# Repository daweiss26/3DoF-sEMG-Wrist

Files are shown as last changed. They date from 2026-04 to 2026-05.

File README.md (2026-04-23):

# Orbita3D Setup Instructions

---

## Prerequisites

You need the following installed on your system:

* **Rust:** Used for compiling the kinematics SDK
* **Python (v3.12 Preferred):** Runs the controller

*Note: These instructions use python and pip commands. You may need to use python3 or pip3 depending on your setup.*

---

## Virtual Environment

It is recommended to create a virtual environment to store compiled packages

*Note: If using PowerShell, you may need to run ```
Set-ExecutionPolicy -ExecutionPolicy RemoteSigned -Scope Process``` first if activation is disabled.*

Create virtual environment (.venv recommended: Other environment names may require file changes such as run_camera_demo.bat)
```
python -m venv .venv
```

Activate virtual environment
```
.venv\Scripts\activate // Windows
source .venv/bin/activate // Mac/Linux
```

---

## Installation

Install the dependencies in the requirements.txt file:
```
pip install -r requirements.txt
```

Then install the Orbita3D package. Inside ```orbita3d_control/orbita3d_c_api```, run:
```
pip install -e .
```

---

## Firmware

Upload the Orbitarduinamixel project to your Generic STM32G4 Series device. Custom-installed libraries should be included in the project.

You may need to add the following .json file for additional boards in the Board Manager:
```
https://github.com/stm32duino/BoardManagerFiles/raw/main/package_stmicroelectronics_index.json
```

The libraries installed:
* **[Simple FOC](https://docs.simplefoc.com/):** by Simplefoc
* **[SimpleFOCDrivers](https://docs.simplefoc.com/):** by Simplefoc
* **[Dynamixel2Arduino](https://github.com/ROBOTIS-GIT/dynamixel2arduino):** by ROBOTIS
* **[Bolder Flight Systems BMI088](https://github.com/bolderflight/bmi088-arduino):** by Brian Taylor

---

## Use

*If using VSCode (recommended), ensure the project contains a ```.vscode``` file with:*
```
{
    "python-envs.defaultEnvManager": "ms-python.python:venv",
    "python.terminal.useEnvFile": true
}
```
Or, in your terminal, ```".:./src:./src/controller:./src/util"``` to your PYTHONPATH environment variable, such as with ```export PYTHONPATH=".:./src:./src/controller:./src/util:$PYTHONPATH"``` for Mac/Linux. For Windows, ```run_camera_demo.bat``` should take care of this.

If using Windows: running ```run_camera_demo.bat``` should work. *Note: You may need to change the specific virtual environment listed in the .bat file if you are using something different from .venv*

If using Mac/Linux: simply run a demo script from the project root directory such as ```python src/orbita_abh_camera.py```

*Note: If using a demo script, you will need to change the Ability Hand serial port in ```src/orbita_abh_camera.py``` and the Orbita3D serial port in ```config/default.yaml``` based upon your device setup. You will likely also need to alter the camera index in ```src/orbita_abh_camera.py``` depending on your setup.*

* **orbita_abh_camera.py:** Uses camera landmarks
* **orbita_emg.py:** Uses muscular signal and a residual TCN model
* **orbita_emg_krr.py:** Uses muscular signal and a kernel ridge regression model
* **task:** Contains landmarker tasks
* **config:** Contains .yaml files for Orbita3D setup. *Contains the serial port to use, which is determined by your specific device.*
* **orbita3d_control:** Contains kinematics for Orbita3D control.
* **firmware:** Contains Arduino code for Orbita3D
* **src/controller:** Contains controller classes for Orbita3D and Ability Hand
* **src/data_collection:** Contains tools for determining electromechanical delay and collecting data
* **src/train:** Contains tools for training muscular signal decoders using collected data
* **src/util:** Contains utilities such as the pose landmarker and coordinate transformer classes

---

## Sources

* **[Orbita3D](https://github.com/pollen-robotics/Orbita_3d_R1):** Original actuator design
* **[Orbita3D Control](https://github.com/pollen-robotics/orbita3d_control):** Generates the kinematics SDK
* **[Rustypot](https://github.com/pollen-robotics/rustypot):** Used to configure servos
* **[Ability Hand API](https://github.com/psyonicinc/ability-hand-api):** Reference on controlling PSYONIC Ability Hand

---

## Docker

You can also run the camera demo through Docker instead of creating a local Python environment if you are using Linux or an OS where Docker is not run on a virtual machine. The Docker image installs the Python dependencies from `requirements.txt`, builds and installs the local `orbita3d_control/orbita3d_c_api` package, and starts `src/orbita_abh_camera.py`.

### Build the image

From the project root, run:
```
docker build --platform linux/amd64 -t orbita-camera-demo .
```

### Run the container

The script needs access to your camera and, if you are controlling hardware, your serial devices. It also opens an OpenCV display window, so on Linux you will typically need to share your X11 socket. A common Linux example is:

```
docker run --platform linux/amd64 --rm -it \
  --device /dev/video0:/dev/video0 \
  --device /dev/ttyUSB0:/dev/ttyUSB0 \
  -e DISPLAY=$DISPLAY \
  -v /tmp/.X11-unix:/tmp/.X11-unix \
  orbita-camera-demo \
  --camera_index 0 \
  --hand_port /dev/ttyUSB0 \
  --orbita_config ./config/default.yaml
```

### Notes

* Update `config/default.yaml` so its `serial_port` matches the Orbita device inside the container, such as `/dev/ttyUSB1` or `/dev/serial/by-id/...`.
* The Ability Hand port is now configurable through `--hand_port`, which is helpful because Linux device names differ from macOS names such as `/dev/cu.usbserial-*`.
* If you only want to test the vision pipeline without connected hardware, you can add `--disable_wrist --disable_hand`.
* If your camera is exposed under a different device path or index, adjust `--device` and `--camera_index` accordingly.
* On macOS or Windows, Docker Desktop does not pass host cameras and serial devices into Linux containers as directly as native Linux does. For full hardware access, running the container on a Linux host is the simplest path.

### Pass different script arguments

Anything placed after the image name is forwarded to `src/orbita_abh_camera.py`. For example:

```
docker run --rm -it \
  --device /dev/video0:/dev/video0 \
  -e DISPLAY=$DISPLAY \
  -v /tmp/.X11-unix:/tmp/.X11-unix \
  orbita-camera-demo \
  --disable_wrist --disable_hand --camera_index 0 --use_elbow
```

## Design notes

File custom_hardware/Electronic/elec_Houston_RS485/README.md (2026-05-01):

# Houston Electronic Board

Houston board is basically a STM32G4 microcontroller that focuses on driving 3 BLDC motors. It gets 3 Hall effects or encoders on motors and absolute positions behind reduction through SPI encoders.

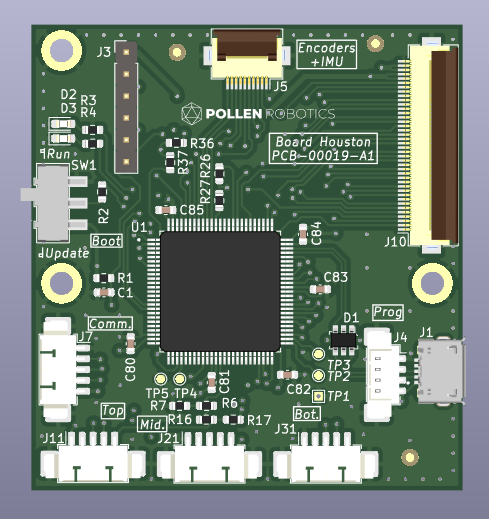
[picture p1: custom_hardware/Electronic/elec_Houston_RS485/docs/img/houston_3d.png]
houston board 3d image


## Basically
 - 50 x 54 mm
 - Powered in 3V3 through the large flat flexible connector J10
 - 5V should also be provided since it supplies encoders J11/21/31
 - Designed with KiCAD 6.0

## ST configuration

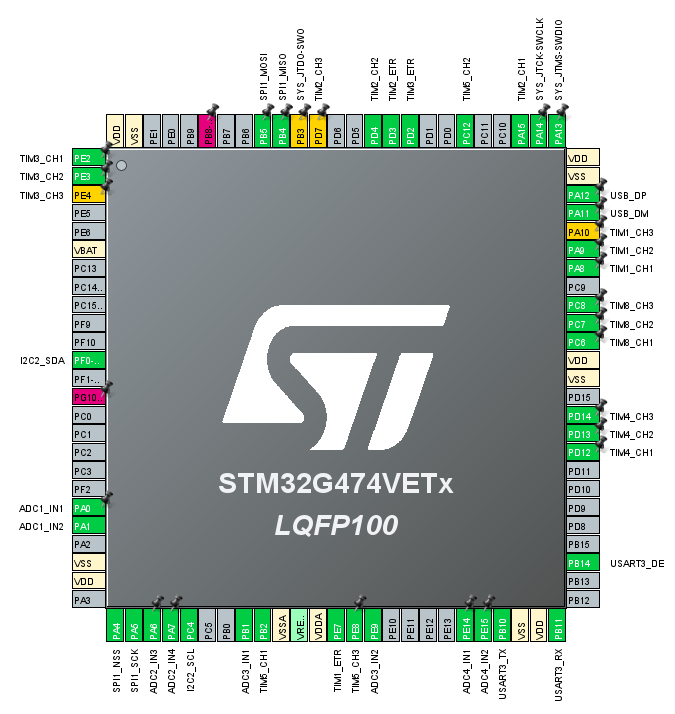
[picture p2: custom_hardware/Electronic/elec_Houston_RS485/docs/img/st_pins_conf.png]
houston board 3d image


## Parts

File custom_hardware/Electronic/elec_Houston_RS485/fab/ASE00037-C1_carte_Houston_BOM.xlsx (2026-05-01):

ASE00037 | C1 | Houston | 2023-04-14
Ref. | Value | Description | Qtty | Man. | Man. Ref.
C1, C80, C81, C82, C83, C84, C85 | 100n 6V3 | Capa 0603 | 7 | TDK | CGA3E2X7R1H104K080AA
D1 | USBLC6-2SC6 | ESD Protection | 1 | STMicro | USBLC6-2SC6
D2 | Green | Green LED 0603 | 1 | Wurth | 150060VS75000
D3 | Red | Red LED 0603 | 1 | Wurth | 150060RS75000
H5 | PCB00019 | PCB | 1
J1 | 10118194-0001LF | USB Prog Connector | 1 | Amphenol FCI | 10118194-0001LF
J2 | Pico3 | Comm. Connector | 1 | Molex | 53261-0371
J3 | DNP - SIL6 | SWDebug Connector | 1 | Harwin | M20-9990646
J4 | Pico4 | Fake USB Connector | 1 | Molex | 53398-0471
J5 | FFC 0,5 mm 10w | Encoders/IMU Connector | 1 | Hirose | FH12-10S-0.5SH(55)
J11, J21, J31 | Pico5 | Comm. Connector | 3 | Molex | 53261-0571
J10 | FFC 0,5 mm 40w | Microcontroller Connector | 1 | Hirose | FH12-40S-0.5SH(55)
R1 | 100k | Res. 0603 | 1 | Yageo | RC0603FR-07100KL
R2 | 10k | Res. 0603 | 1 | Yageo | RC0603FR-0710KL
R3, R4 | 470R | Res. 0603 | 2 | Yageo | RC0603FR-07470RL
R6 | DNP-4k7 | Res. 0603 | 1
R7 | DNP-9k1 | Res. 0603 | 1
R17, R27, R38, R39 | 0R | Res. 0603 | 4 | Yageo | RC0603FR-070RL
R26, R36, R37, R40 | DNP-0R | Res. 0603 | 4
SW1 | SW_SPDT | Boot switch | 1 | C&K Switches | JS102011SAQN
U1 | STM32G474 | Microcontroller | 1 | STMicro | STM32G474VET6

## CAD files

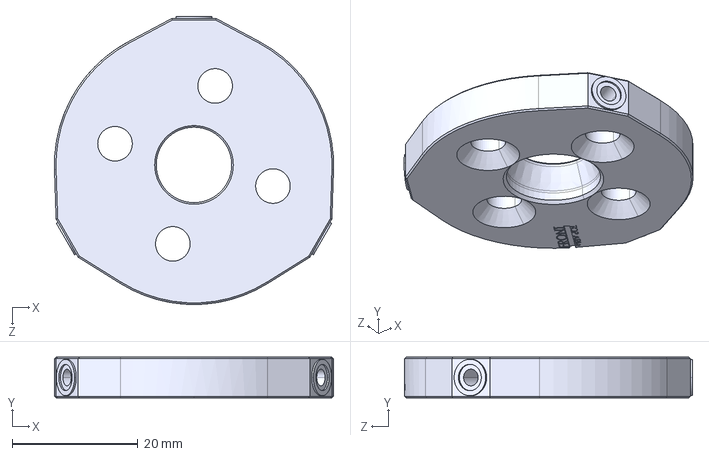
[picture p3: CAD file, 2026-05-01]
custom_hardware/Mechanical/Adapter/ResearchWristAdapter.STEP
44.4 x 6.50 x 45.8 mm

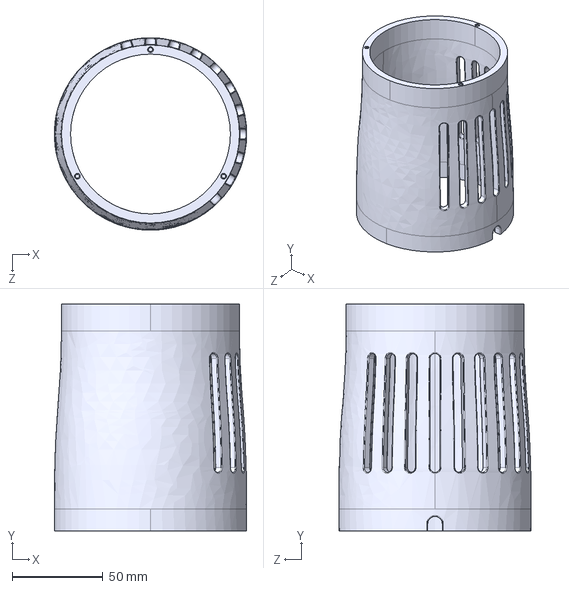
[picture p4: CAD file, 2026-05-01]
custom_hardware/Mechanical/Enclosure/EnclosureBody.STEP
106.0 x 125.0 x 106.0 mm

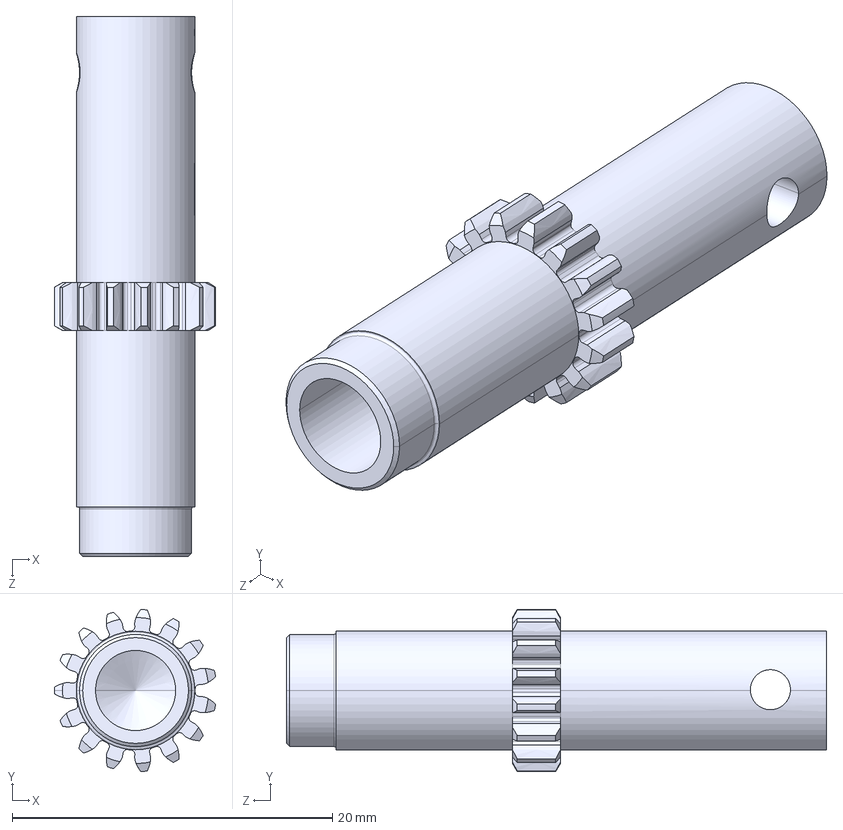
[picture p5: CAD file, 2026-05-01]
custom_hardware/Mechanical/Gears/MiddlePinion.STEP
10.1 x 10.1 x 33.7 mm

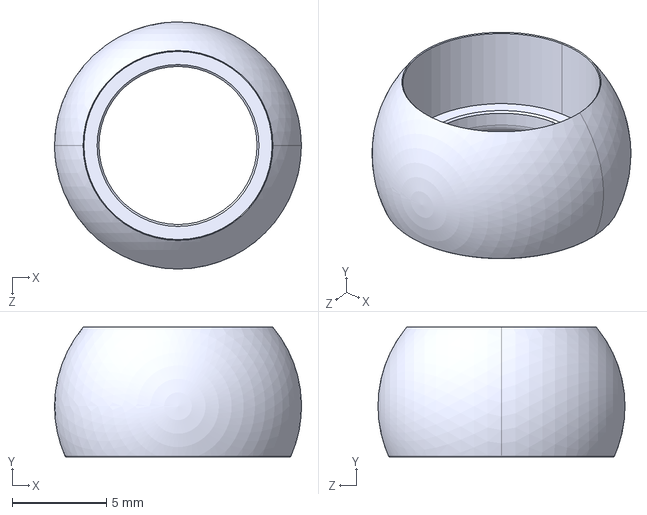
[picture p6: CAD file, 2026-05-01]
custom_hardware/Mechanical/Adapter/ResearchBall.STEP
13.1 x 6.89 x 13.1 mm

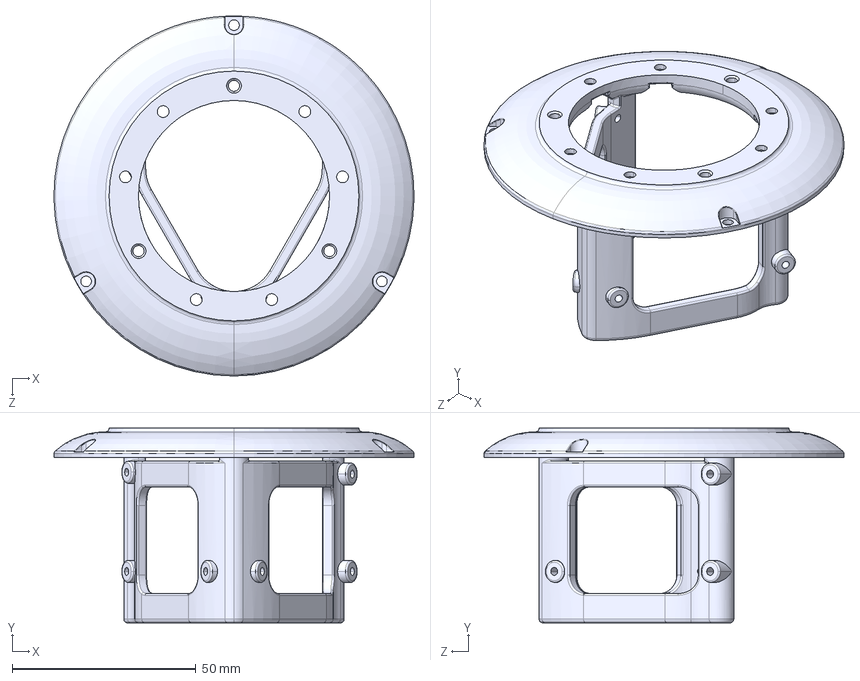
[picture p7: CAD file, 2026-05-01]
custom_hardware/Mechanical/Enclosure/EnclosureTopWithPCBHolder.STEP
98.0 x 53.0 x 98.0 mm

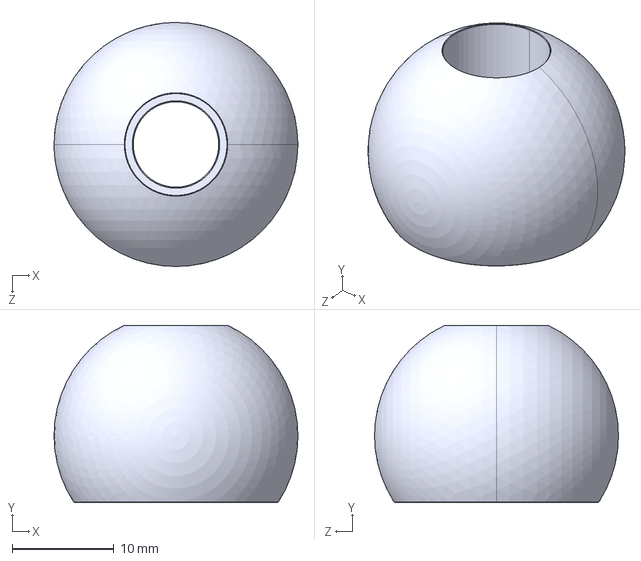
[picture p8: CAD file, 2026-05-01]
custom_hardware/Mechanical/Adapter/LaminationBall.STEP
24.0 x 17.5 x 24.0 mm

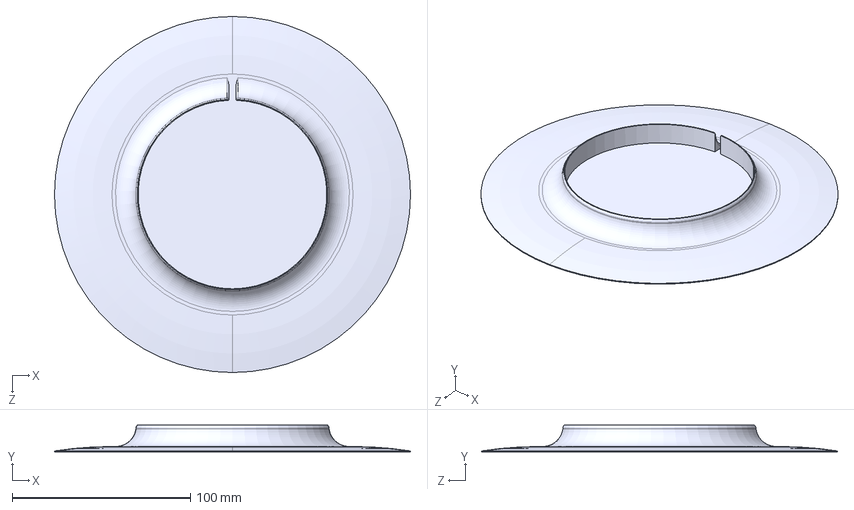
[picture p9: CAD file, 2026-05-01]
custom_hardware/Mechanical/Enclosure/EnclosureBottom.STEP
200.0 x 15.0 x 200.0 mm

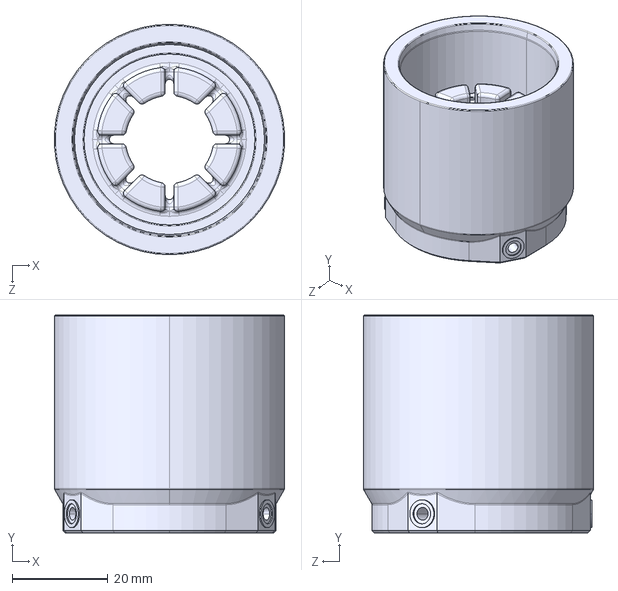
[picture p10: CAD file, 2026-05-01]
custom_hardware/Mechanical/Adapter/LaminationWristAdapter.STEP
47.9 x 45.4 x 48.0 mm

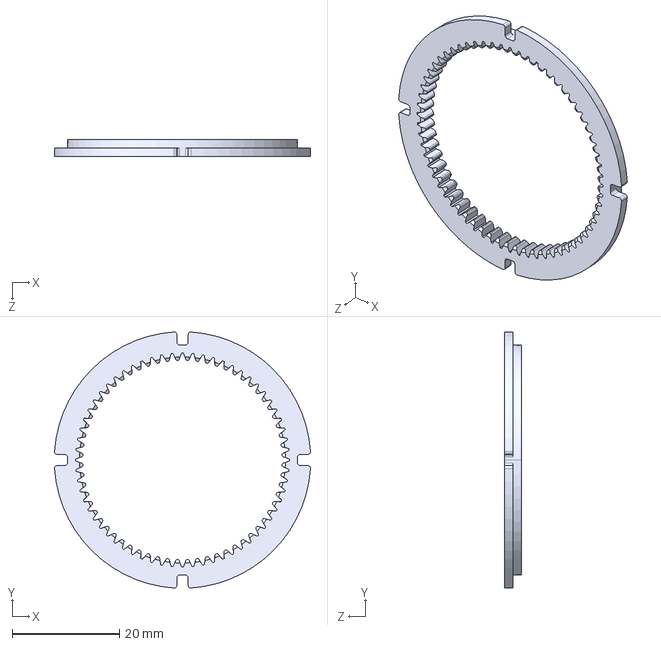
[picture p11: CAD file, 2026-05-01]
custom_hardware/Mechanical/Gears/InternalGear.STEP
47.8 x 47.8 x 3.20 mm

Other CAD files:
custom_hardware/Mechanical/Gears/TopPinion.STEP
custom_hardware/Mechanical/Gears/BottomPinion_Dslot.STEP
custom_hardware/Mechanical/Gears/MiddlePinion_Dslot.STEP
custom_hardware/Mechanical/Gears/TopPinion_Dslot.STEP
custom_hardware/Mechanical/Gears/BottomPinion.STEP

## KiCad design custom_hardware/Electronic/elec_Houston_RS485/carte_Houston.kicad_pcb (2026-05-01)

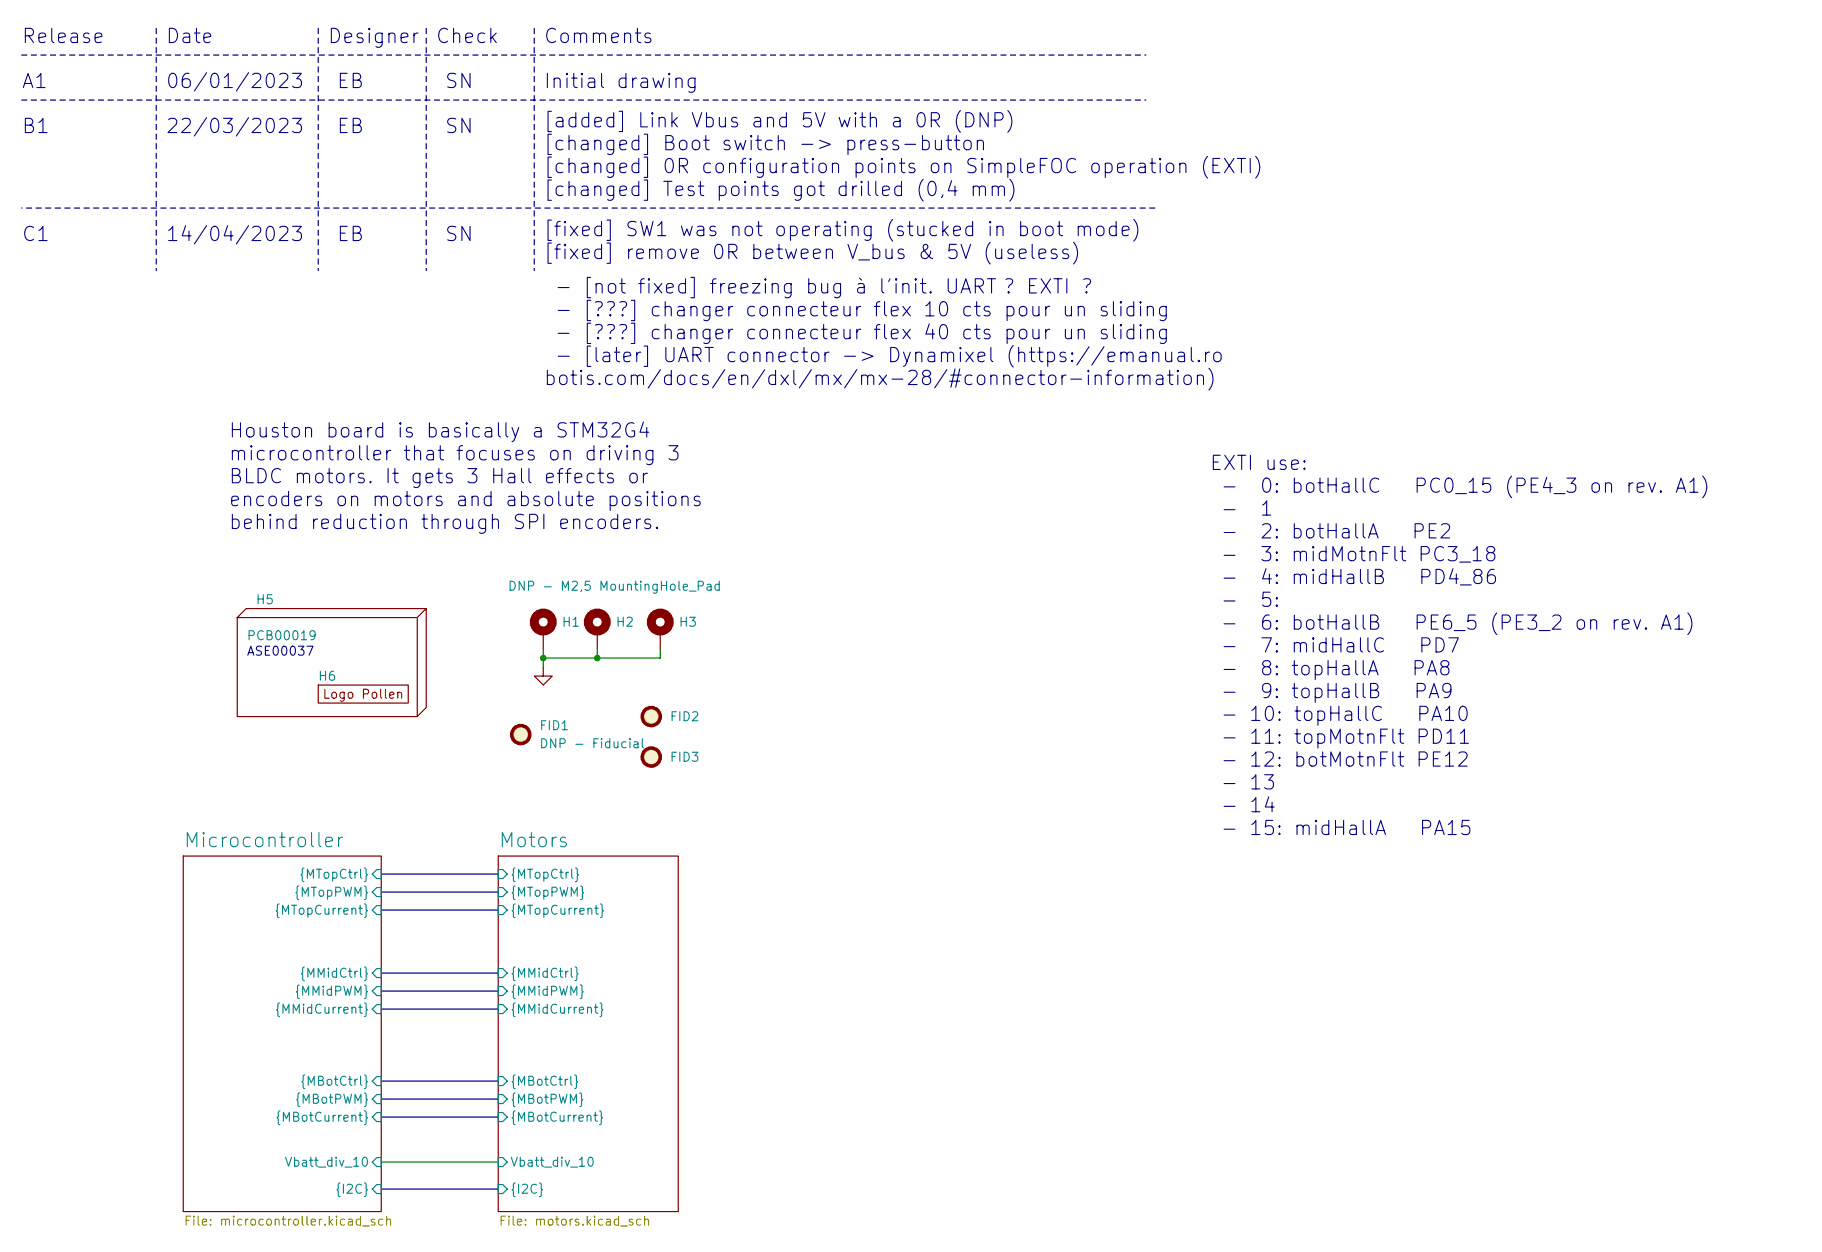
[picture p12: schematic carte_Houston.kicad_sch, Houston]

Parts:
FID1, FID2, FID3: DNP - Fiducial; Fiducial_1mm_Mask2mm
H1, H2, H3: DNP - M2,5 MountingHole_Pad; MountingHole_2.7mm_M2.5_DIN965_Pad_TopOnly
H5: PCB00019
H6: DNP - Logo Pollen 2021; Logo_Pollen_2021

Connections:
GND: H1.1, H2.1, H3.1; also elsewhere on the board

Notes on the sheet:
Date
Check
Release
[added] Link Vbus and 5V with a 0R (DNP) [changed] Boot switch -> press-button [changed] 0R configuration points on SimpleFOC operation (EXTI) [changed] Test points got drilled (0,4 mm)
ASE00037
22/03/2023
- [not fixed] freezing bug à l'init. UART ? EXTI ? - [???] changer connecteur flex 10 cts pour un sliding - [???] changer connecteur flex 40 cts pour un sliding - [later] UART connector -> Dynamixel (https://emanual.ro botis.com/docs/en/dxl/mx/mx-28/#connector-information)
Initial drawing
[fixed] SW1 was not operating (stucked in boot mode) [fixed] remove 0R between V_bus & 5V (useless)
EXTI use: - 0: botHallC PC0_15 (PE4_3 on rev. A1) - 1 - 2: botHallA PE2 - 3: midMotnFlt PC3_18 - 4: midHallB PD4_86 - 5: - 6: botHallB PE6_5 (PE3_2 on rev. A1) - 7: midHallC PD7 - 8: topHallA PA8 - 9: topHallB PA9 - 10: topHallC PA10 - 11: topMotnFlt PD11 - 12: botMotnFlt PE12 - 13 - 14 - 15: midHa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
Designer
14/04/2023
Houston board is basically a STM32G4 microcontroller that focuses on driving 3 BLDC motors. It gets 3 Hall effects or encoders on motors and absolute positions behind reduction through SPI encoders.
Comments
06/01/2023

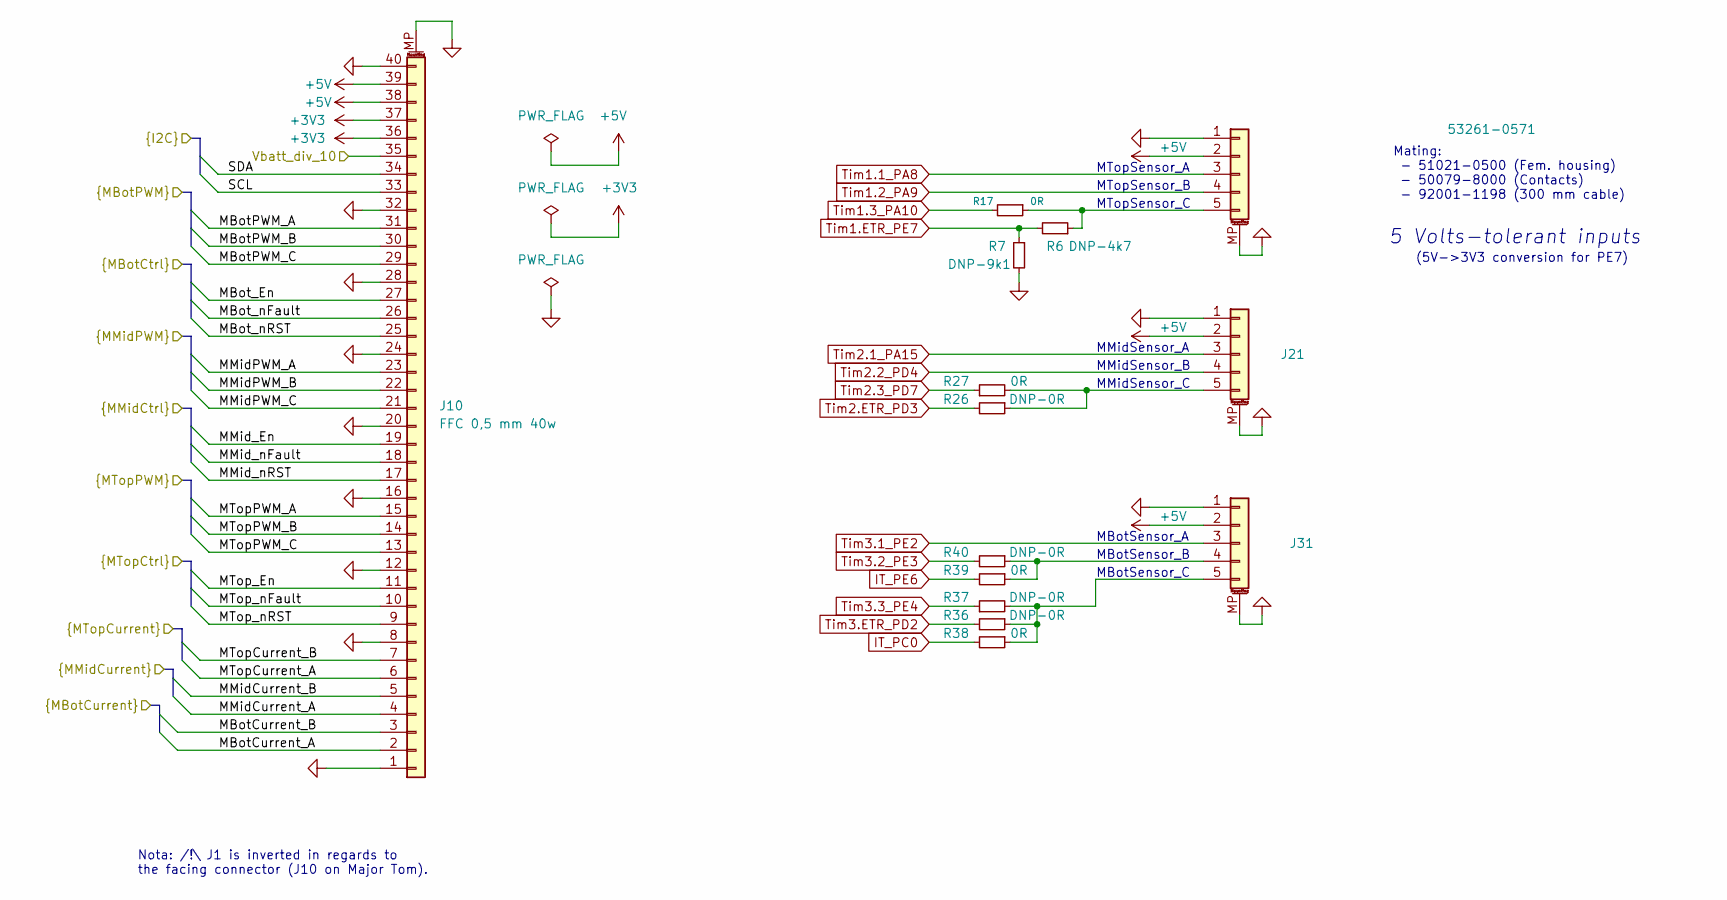
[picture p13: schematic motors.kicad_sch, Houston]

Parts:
J10: FFC 0,5 mm 40w; Hirose_FH12-40S-0.5SH_1x40-1MP_P0.50mm_Horizontal
J11: PicoBlade5; Molex_PicoBlade_53261-0571_1x05-1MP_P1.25mm_Horizontal
J21, J31: Pico5; Molex_PicoBlade_53261-0571_1x05-1MP_P1.25mm_Horizontal
R6: DNP-4k7; R_0603_1608Metric
R7: DNP-9k1; R_0603_1608Metric
R17, R27, R38, R39: 0R; R_0603_1608Metric
R26, R36, R37, R40: DNP-0R; R_0603_1608Metric

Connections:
+3V3: J10.36, J10.37; also elsewhere on the board
+5V: J10.38, J10.39, J11.2, J21.2, J31.2; also elsewhere on the board
/Microcontroller/MBotCurrent_A: J10.2; also elsewhere on the board
/Microcontroller/MBotCurrent_B: J10.3; also elsewhere on the board
/Microcontroller/MBotPWM_A: J10.31; also elsewhere on the board
/Microcontroller/MBotPWM_B: J10.30; also elsewhere on the board
/Microcontroller/MBotPWM_C: J10.29; also elsewhere on the board
/Microcontroller/MBot_En: J10.27; also elsewhere on the board
/Microcontroller/MBot_nFault: J10.26; also elsewhere on the board
/Microcontroller/MBot_nRST: J10.25; also elsewhere on the board
/Microcontroller/MMidCurrent_A: J10.4; also elsewhere on the board
/Microcontroller/MMidCurrent_B: J10.5; also elsewhere on the board
/Microcontroller/MMidPWM_A: J10.23; also elsewhere on the board
/Microcontroller/MMidPWM_B: J10.22; also elsewhere on the board
/Microcontroller/MMidPWM_C: J10.21; also elsewhere on the board
/Microcontroller/MMid_En: J10.19; also elsewhere on the board
/Microcontroller/MMid_nFault: J10.18; also elsewhere on the board
/Microcontroller/MMid_nRST: J10.17; also elsewhere on the board
/Microcontroller/MTopCurrent_A: J10.6; also elsewhere on the board
/Microcontroller/MTopCurrent_B: J10.7; also elsewhere on the board
/Microcontroller/MTopPWM_A: J10.15; also elsewhere on the board
/Microcontroller/MTopPWM_B: J10.14; also elsewhere on the board
/Microcontroller/MTopPWM_C: J10.13; also elsewhere on the board
/Microcontroller/MTop_En: J10.11; also elsewhere on the board
/Microcontroller/MTop_nFault: J10.10; also elsewhere on the board
/Microcontroller/MTop_nRST: J10.9; also elsewhere on the board
/Microcontroller/SCL: J10.33; also elsewhere on the board
/Microcontroller/SDA: J10.34; also elsewhere on the board
/Microcontroller/Vbatt_div_10: J10.35; also elsewhere on the board
GND: J10.1, J10.8, J10.12, J10.16, J10.20, J10.24, J10.28, J10.32, J10.40, J10.MP (MountPin), J11.1, J11.MP (MountPin), J21.1, J21.MP (MountPin), J31.1, J31.MP (MountPin), R7.2; also elsewhere on the board
IT_PC0: R38.2; also elsewhere on the board
IT_PE6: R39.2; also elsewhere on the board
unnamed: J11.5, R6.1, R17.1
unnamed: J21.5, R26.1, R27.2
unnamed: J31.4, R39.1, R40.1
unnamed: J31.5, R36.1, R37.2, R38.1
Tim1.1_PA8: J11.3; also elsewhere on the board
Tim1.2_PA9: J11.4; also elsewhere on the board
Tim1.3_PA10: R17.2; also elsewhere on the board
Tim1.ETR_PE7: R6.2, R7.1; also elsewhere on the board
Tim2.1_PA15: J21.3; also elsewhere on the board
Tim2.2_PD4: J21.4; also elsewhere on the board
Tim2.3_PD7: R27.1; also elsewhere on the board
Tim2.ETR_PD3: R26.2; also elsewhere on the board
Tim3.1_PE2: J31.3; also elsewhere on the board
Tim3.2_PE3: R40.2; also elsewhere on the board
Tim3.3_PE4: R37.1; also elsewhere on the board
Tim3.ETR_PD2: R36.2; also elsewhere on the board

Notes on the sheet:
MTopSensor_B
MBotSensor_A
MBotSensor_C
MTopSensor_C
MMidSensor_A
(5V->3V3 conversion for PE7)
MBotSensor_B
MTopSensor_A
MMidSensor_B
5 Volts-tolerant inputs
Nota: /!\ J1 is inverted in regards to the facing connector (J10 on Major Tom).
Mating: - 51021-0500 (Fem. housing) - 50079-8000 (Contacts) - 92001-1198 (300 mm cable)
MMidSensor_C

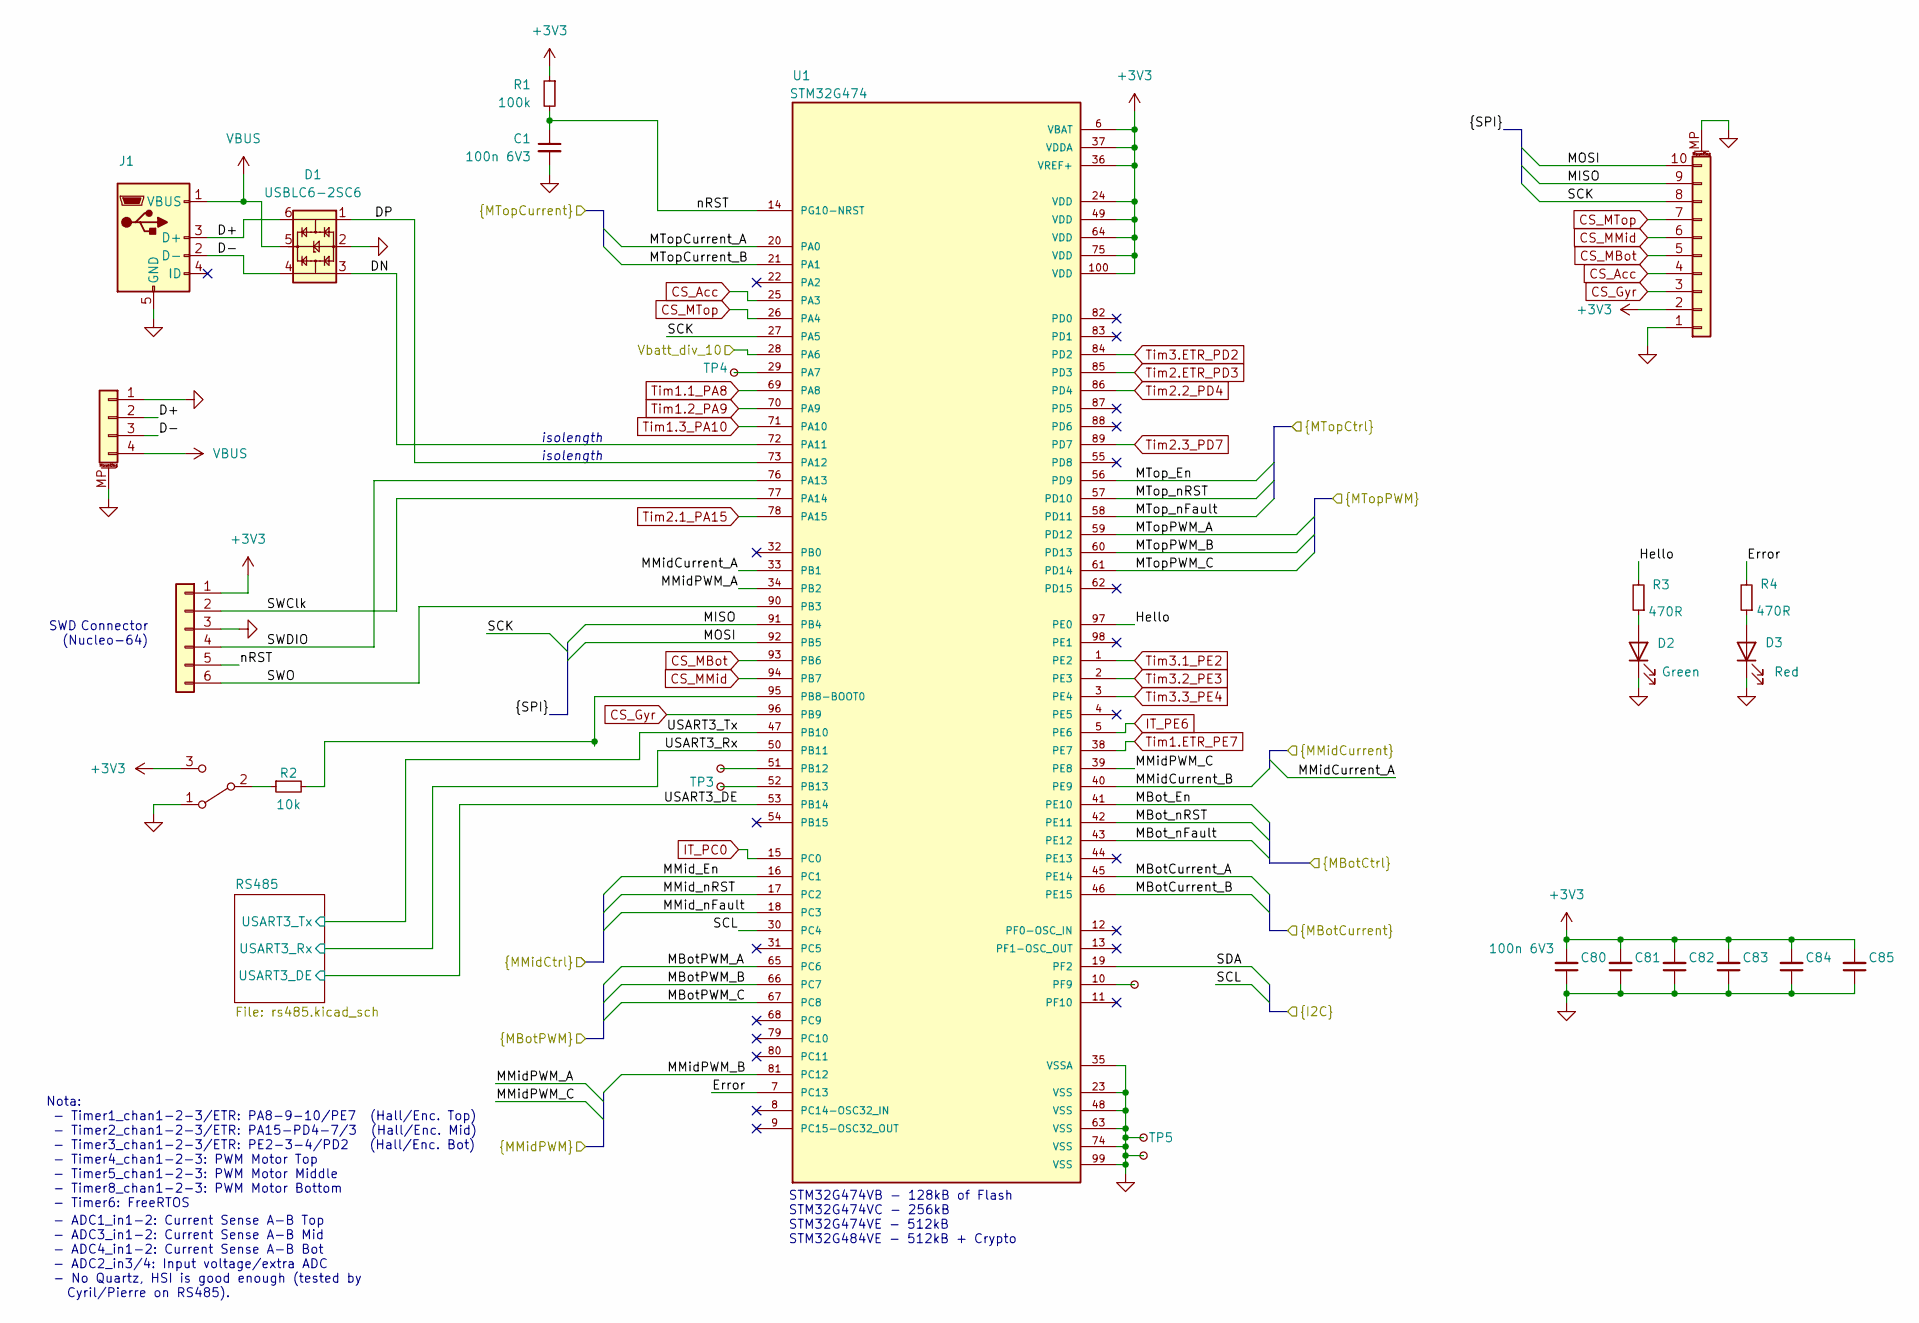
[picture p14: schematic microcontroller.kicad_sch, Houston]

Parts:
C1, C80, C81, C82, C83, C84, C85: 100n 6V3; C_0603_1608Metric
D1: USBLC6-2SC6; SOT23-6L
D2: Green; LED_0603_1608Metric_Pad1.05x0.95mm_HandSolder
D3: Red; LED_0603_1608Metric_Pad1.05x0.95mm_HandSolder
J1: 10118194-0001LF; Amphenol_10118194-0001LF
J3: SIL6; PinHeader_1x06_P2.54mm_Vertical
J4: PicoBlade4; Molex_PicoBlade_53398-0471_1x04-1MP_P1.25mm_Vertical
J5: Conn_01x10_MountingPin; Hirose_FH12-10S-0.5SH_1x10-1MP_P0.50mm_Horizontal
R1: 100k; R_0603_1608Metric
R2: 10k; R_0603_1608Metric
R3, R4: 470R; R_0603_1608Metric
SW1: SW_SPDT; SW_SPDT_CK-JS102011SAQN
TP1: DNP TestPoint_Small; TestPoint_THTPad_2.0x2.0mm_Drill1.0mm
TP2, TP6: DNP TestPoint_Small; TestPoint_Pad_D1.0mm
TP3, TP4, TP5: DNP - TestPoint_Small; TestPoint_THTPad_D1.0mm_Drill0.4mm
U1: STM32G474; QFP50P1600X1600X160-100N

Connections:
+3V3: C80.2, C81.2, C82.2, C83.2, C84.2, C85.2, J3.1, J5.2, R1.1, SW1.3 (C), U1.6 (VBAT), U1.24 (VDD), U1.36 (VREF+), U1.37 (VDDA), U1.49 (VDD), U1.64 (VDD), U1.75 (VDD), U1.100 (VDD); also elsewhere on the board
/Microcontroller/D+: D1.6, J1.3 (D+), J4.2
/Microcontroller/D-: D1.4, J1.2 (D-), J4.3
/Microcontroller/DN: D1.3, U1.72 (PA11)
/Microcontroller/DP: D1.1, U1.73 (PA12)
/Microcontroller/Error: R4.2, U1.7 (PC13)
/Microcontroller/Hello: R3.2, U1.97 (PE0)
/Microcontroller/MBotCurrent_A: U1.45 (PE14); also elsewhere on the board
/Microcontroller/MBotCurrent_B: U1.46 (PE15); also elsewhere on the board
/Microcontroller/MBotPWM_A: U1.65 (PC6); also elsewhere on the board
/Microcontroller/MBotPWM_B: U1.66 (PC7); also elsewhere on the board
/Microcontroller/MBotPWM_C: U1.67 (PC8); also elsewhere on the board
/Microcontroller/MBot_En: U1.41 (PE10); also elsewhere on the board
/Microcontroller/MBot_nFault: U1.43 (PE12); also elsewhere on the board
/Microcontroller/MBot_nRST: U1.42 (PE11); also elsewhere on the board
/Microcontroller/MISO: J5.9, U1.91 (PB4)
/Microcontroller/MMidCurrent_A: U1.33 (PB1); also elsewhere on the board
/Microcontroller/MMidCurrent_B: U1.40 (PE9); also elsewhere on the board
/Microcontroller/MMidPWM_A: U1.34 (PB2); also elsewhere on the board
/Microcontroller/MMidPWM_B: U1.81 (PC12); also elsewhere on the board
/Microcontroller/MMidPWM_C: U1.39 (PE8); also elsewhere on the board
/Microcontroller/MMid_En: U1.16 (PC1); also elsewhere on the board
/Microcontroller/MMid_nFault: U1.18 (PC3); also elsewhere on the board
/Microcontroller/MMid_nRST: U1.17 (PC2); also elsewhere on the board
/Microcontroller/MOSI: J5.10, U1.92 (PB5)
/Microcontroller/MTopCurrent_A: U1.20 (PA0); also elsewhere on the board
/Microcontroller/MTopCurrent_B: U1.21 (PA1); also elsewhere on the board
/Microcontroller/MTopPWM_A: U1.59 (PD12); also elsewhere on the board
/Microcontroller/MTopPWM_B: U1.60 (PD13); also elsewhere on the board
/Microcontroller/MTopPWM_C: U1.61 (PD14); also elsewhere on the board
/Microcontroller/MTop_En: U1.56 (PD9); also elsewhere on the board
/Microcontroller/MTop_nFault: U1.58 (PD11); also elsewhere on the board
/Microcontroller/MTop_nRST: U1.57 (PD10); also elsewhere on the board
/Microcontroller/SCK: J5.8, U1.27 (PA5)
/Microcontroller/SCL: U1.30 (PC4); also elsewhere on the board
/Microcontroller/SDA: U1.19 (PF2); also elsewhere on the board
/Microcontroller/SWClk: J3.2, U1.77 (PA14)
/Microcontroller/SWDIO: J3.4, U1.76 (PA13)
/Microcontroller/SWO: J3.6, U1.90 (PB3)
/Microcontroller/USART3_DE: U1.53 (PB14); also elsewhere on the board
/Microcontroller/USART3_Rx: U1.50 (PB11); also elsewhere on the board
/Microcontroller/USART3_Tx: U1.47 (PB10); also elsewhere on the board
/Microcontroller/Vbatt_div_10: U1.28 (PA6); also elsewhere on the board
/Microcontroller/nRST: C1.1, J3.5, R1.2, U1.14 (PG10-NRST)
CS_Acc: J5.4, U1.25 (PA3)
CS_Gyr: J5.3, U1.96 (PB9)
CS_MBot: J5.5, U1.93 (PB6)
CS_MMid: J5.6, U1.94 (PB7)
CS_MTop: J5.7, U1.26 (PA4)
GND: C1.2, C80.1, C81.1, C82.1, C83.1, C84.1, C85.1, D1.2, D2.1 (K), D3.1 (K), J1.5 (GND), J3.3, J4.1, J4.MP (MountPin), J5.1, J5.MP (MountPin), SW1.1 (A), TP1.1, TP5.1, U1.23 (VSS), U1.35 (VSSA), U1.48 (VSS), U1.63 (VSS), U1.74 (VSS), U1.99 (VSS); also elsewhere on the board
IT_PC0: U1.15 (PC0); also elsewhere on the board
IT_PE6: U1.5 (PE6); also elsewhere on the board
unnamed: D2.2 (A), R3.1
unnamed: D3.2 (A), R4.1
unnamed: R2.1, SW1.2 (B)
unnamed: TP4.1, U1.29 (PA7)
unnamed: R2.2, U1.95 (PB8-BOOT0)
unnamed: TP2.1, U1.51 (PB12)
unnamed: TP3.1, U1.52 (PB13)
unnamed: TP6.1, U1.10 (PF9)
Tim1.1_PA8: U1.69 (PA8); also elsewhere on the board
Tim1.2_PA9: U1.70 (PA9); also elsewhere on the board
Tim1.3_PA10: U1.71 (PA10); also elsewhere on the board
Tim1.ETR_PE7: U1.38 (PE7); also elsewhere on the board
Tim2.1_PA15: U1.78 (PA15); also elsewhere on the board
Tim2.2_PD4: U1.86 (PD4); also elsewhere on the board
Tim2.3_PD7: U1.89 (PD7); also elsewhere on the board
Tim2.ETR_PD3: U1.85 (PD3); also elsewhere on the board
Tim3.1_PE2: U1.1 (PE2); also elsewhere on the board
Tim3.2_PE3: U1.2 (PE3); also elsewhere on the board
Tim3.3_PE4: U1.3 (PE4); also elsewhere on the board
Tim3.ETR_PD2: U1.84 (PD2); also elsewhere on the board
VBUS: D1.5, J1.1 (VBUS), J4.4

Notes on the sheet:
Nota: - Timer1_chan1-2-3/ETR: PA8-9-10/PE7 (Hall/Enc. Top) - Timer2_chan1-2-3/ETR: PA15-PD4-7/3 (Hall/Enc. Mid) - Timer3_chan1-2-3/ETR: PE2-3-4/PD2 (Hall/Enc. Bot) - Timer4_chan1-2-3: PWM Motor Top - Timer5_chan1-2-3: PWM Motor Middle - Timer8_chan1-2-3: PWM Motor Bottom - Timer6: FreeRTOS
isolength
STM32G474VB - 128kB of Flash STM32G474VC - 256kB STM32G474VE - 512kB STM32G484VE - 512kB + Crypto
SWD Connector (Nucleo-64)
- ADC1_in1-2: Current Sense A-B Top - ADC3_in1-2: Current Sense A-B Mid - ADC4_in1-2: Current Sense A-B Bot - ADC2_in3/4: Input voltage/extra ADC - No Quartz, HSI is good enough (tested by Cyril/Pierre on RS485).

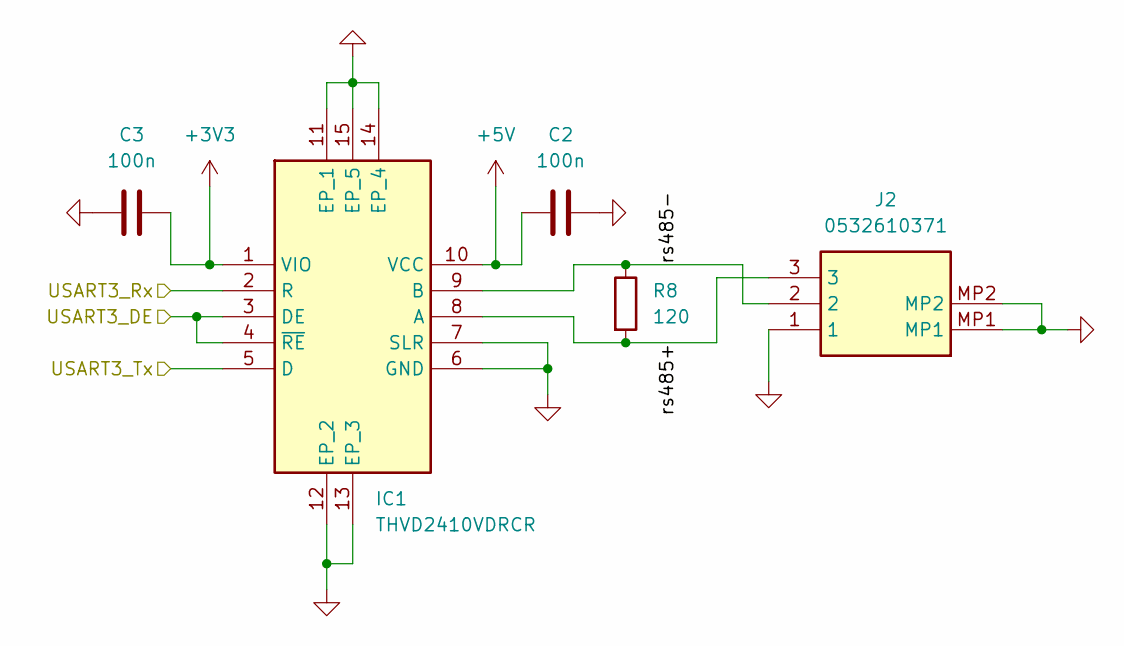
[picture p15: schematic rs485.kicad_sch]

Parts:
C2, C3: 100n; C_0402_1005Metric
IC1: THVD2410VDRCR; TPS259241DRCR; Manufacturer_Part_Number THVD2410VDRCR; Mouser Part Number 595-THVD2410VDRCR
J2: 0532610371; Manufacturer_Part_Number 0532610371
R8: 120; R_0402_1005Metric

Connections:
+3V3: C3.2, IC1.1 (VIO); also elsewhere on the board
+5V: C2.1, IC1.10 (VCC); also elsewhere on the board
/Microcontroller/RS485/rs485+: IC1.8 (A), J2.3, R8.2
/Microcontroller/RS485/rs485-: IC1.9 (B), J2.2, R8.1
/Microcontroller/USART3_DE: IC1.3 (DE), IC1.4 (~RE); also elsewhere on the board
/Microcontroller/USART3_Rx: IC1.2 (R); also elsewhere on the board
/Microcontroller/USART3_Tx: IC1.5 (D); also elsewhere on the board
GND: C2.2, C3.1, IC1.6 (GND), IC1.7 (SLR), IC1.11 (EP_1), IC1.12 (EP_2), IC1.13 (EP_3), IC1.14 (EP_4), IC1.15 (EP_5), J2.1, J2.MP1, J2.MP2; also elsewhere on the board

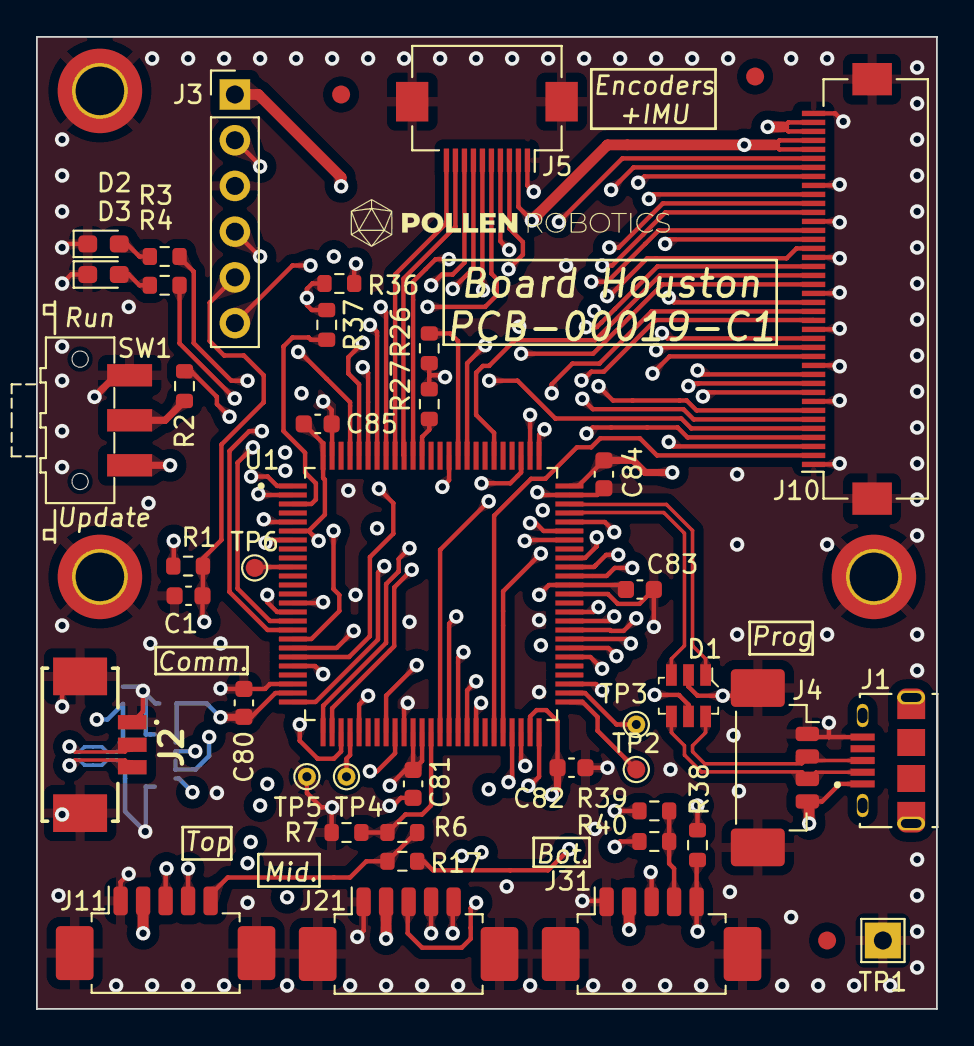
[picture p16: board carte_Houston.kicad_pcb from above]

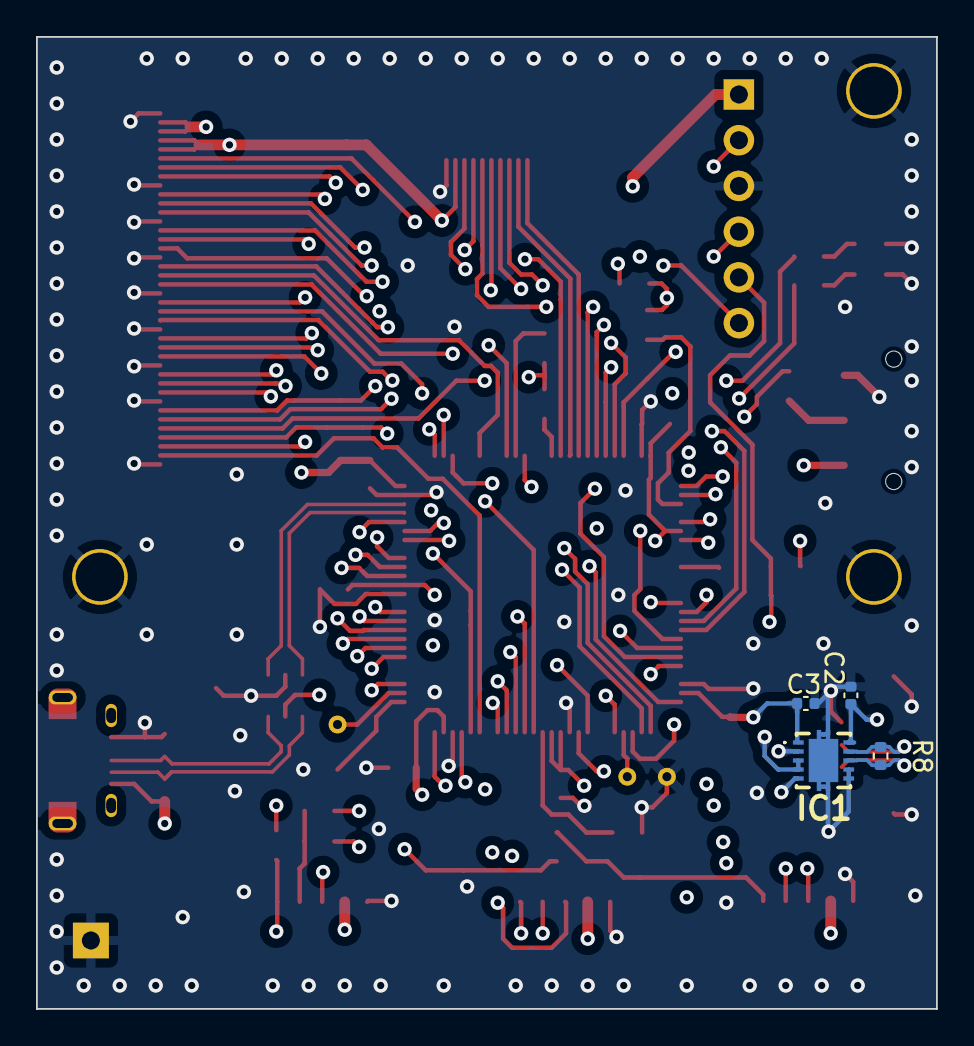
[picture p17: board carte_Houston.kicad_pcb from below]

Board: 4 copper layers, 50.0 x 54.0 mm, 52 parts (4 on the bottom side), 80 nets.

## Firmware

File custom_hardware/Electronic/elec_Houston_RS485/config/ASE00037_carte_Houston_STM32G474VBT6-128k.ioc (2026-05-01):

#MicroXplorer Configuration settings - do not modify
ADC1.Channel-0\#ChannelRegularConversion=ADC_CHANNEL_1
ADC1.CommonPathInternal=null|null|null|null
ADC1.IPParameters=Rank-0\#ChannelRegularConversion,Channel-0\#ChannelRegularConversion,SamplingTime-0\#ChannelRegularConversion,OffsetNumber-0\#ChannelRegularConversion,NbrOfConversionFlag,master,CommonPathInternal
ADC1.NbrOfConversionFlag=1
ADC1.OffsetNumber-0\#ChannelRegularConversion=ADC_OFFSET_NONE
ADC1.Rank-0\#ChannelRegularConversion=1
ADC1.SamplingTime-0\#ChannelRegularConversion=ADC_SAMPLETIME_2CYCLES_5
ADC1.master=1
ADC2.Channel-1\#ChannelRegularConversion=ADC_CHANNEL_3
ADC2.CommonPathInternal=null|null|null|null
ADC2.IPParameters=Rank-1\#ChannelRegularConversion,Channel-1\#ChannelRegularConversion,SamplingTime-1\#ChannelRegularConversion,OffsetNumber-1\#ChannelRegularConversion,NbrOfConversionFlag,CommonPathInternal
ADC2.NbrOfConversionFlag=1
ADC2.OffsetNumber-1\#ChannelRegularConversion=ADC_OFFSET_NONE
ADC2.Rank-1\#ChannelRegularConversion=1
ADC2.SamplingTime-1\#ChannelRegularConversion=ADC_SAMPLETIME_2CYCLES_5
ADC3.Channel-0\#ChannelRegularConversion=ADC_CHANNEL_1
ADC3.CommonPathInternal=null|null|null|null
ADC3.IPParameters=Rank-0\#ChannelRegularConversion,Channel-0\#ChannelRegularConversion,SamplingTime-0\#ChannelRegularConversion,OffsetNumber-0\#ChannelRegularConversion,NbrOfConversionFlag,master,CommonPathInternal
ADC3.NbrOfConversionFlag=1
ADC3.OffsetNumber-0\#ChannelRegularConversion=ADC_OFFSET_NONE
ADC3.Rank-0\#ChannelRegularConversion=1
ADC3.SamplingTime-0\#ChannelRegularConversion=ADC_SAMPLETIME_2CYCLES_5
ADC3.master=1
ADC4.Channel-0\#ChannelRegularConversion=ADC_CHANNEL_1
ADC4.CommonPathInternal=null|null|null|null
ADC4.IPParameters=Rank-0\#ChannelRegularConversion,Channel-0\#ChannelRegularConversion,SamplingTime-0\#ChannelRegularConversion,OffsetNumber-0\#ChannelRegularConversion,NbrOfConversionFlag,CommonPathInternal
ADC4.NbrOfConversionFlag=1
ADC4.OffsetNumber-0\#ChannelRegularConversion=ADC_OFFSET_NONE
ADC4.Rank-0\#ChannelRegularConversion=1
ADC4.SamplingTime-0\#ChannelRegularConversion=ADC_SAMPLETIME_2CYCLES_5
Dma.ADC1.0.Direction=DMA_PERIPH_TO_MEMORY
Dma.ADC1.0.EventEnable=DISABLE
Dma.ADC1.0.Instance=DMA1_Channel1
Dma.ADC1.0.MemDataAlignment=DMA_MDATAALIGN_HALFWORD
Dma.ADC1.0.MemInc=DMA_MINC_ENABLE
Dma.ADC1.0.Mode=DMA_NORMAL
Dma.ADC1.0.PeriphDataAlignment=DMA_PDATAALIGN_HALFWORD
Dma.ADC1.0.PeriphInc=DMA_PINC_DISABLE
Dma.ADC1.0.Polarity=HAL_DMAMUX_REQ_GEN_RISING
Dma.ADC1.0.Priority=DMA_PRIORITY_LOW
Dma.ADC1.0.RequestNumber=1
Dma.ADC1.0.RequestParameters=Instance,Direction,PeriphInc,MemInc,PeriphDataAlignment,MemDataAlignment,Mode,Priority,SignalID,Polarity,RequestNumber,SyncSignalID,SyncPolarity,SyncEnable,EventEnable,SyncRequestNumber
Dma.ADC1.0.SignalID=NONE
Dma.ADC1.0.SyncEnable=DISABLE
Dma.ADC1.0.SyncPolarity=HAL_DMAMUX_SYNC_NO_EVENT
Dma.ADC1.0.SyncRequestNumber=1
Dma.ADC1.0.SyncSignalID=NONE
Dma.ADC2.1.Direction=DMA_PERIPH_TO_MEMORY
Dma.ADC2.1.EventEnable=DISABLE
Dma.ADC2.1.Instance=DMA1_Channel2
Dma.ADC2.1.MemDataAlignment=DMA_MDATAALIGN_HALFWORD
Dma.ADC2.1.MemInc=DMA_MINC_ENABLE
Dma.ADC2.1.Mode=DMA_NORMAL
Dma.ADC2.1.PeriphDataAlignment=DMA_PDATAALIGN_HALFWORD
Dma.ADC2.1.PeriphInc=DMA_PINC_DISABLE
Dma.ADC2.1.Polarity=HAL_DMAMUX_REQ_GEN_RISING
Dma.ADC2.1.Priority=DMA_PRIORITY_LOW
Dma.ADC2.1.RequestNumber=1
Dma.ADC2.1.RequestParameters=Instance,Direction,PeriphInc,MemInc,PeriphDataAlignment,MemDataAlignment,Mode,Priority,SignalID,Polarity,RequestNumber,SyncSignalID,SyncPolarity,SyncEnable,EventEnable,SyncRequestNumber
Dma.ADC2.1.SignalID=NONE
Dma.ADC2.1.SyncEnable=DISABLE
Dma.ADC2.1.SyncPolarity=HAL_DMAMUX_SYNC_NO_EVENT
Dma.ADC2.1.SyncRequestNumber=1
Dma.ADC2.1.SyncSignalID=NONE
Dma.ADC3.2.Direction=DMA_PERIPH_TO_MEMORY
Dma.ADC3.2.EventEnable=DISABLE
Dma.ADC3.2.Instance=DMA1_Channel3
Dma.ADC3.2.MemDataAlignment=DMA_MDATAALIGN_HALFWORD
Dma.ADC3.2.MemInc=DMA_MINC_ENABLE
Dma.ADC3.2.Mode=DMA_NORMAL
Dma.ADC3.2.PeriphDataAlignment=DMA_PDATAALIGN_HALFWORD
Dma.ADC3.2.PeriphInc=DMA_PINC_DISABLE
Dma.ADC3.2.Polarity=HAL_DMAMUX_REQ_GEN_RISING
Dma.ADC3.2.Priority=DMA_PRIORITY_LOW
Dma.ADC3.2.RequestNumber=1
Dma.ADC3.2.RequestParameters=Instance,Direction,PeriphInc,MemInc,PeriphDataAlignment,MemDataAlignment,Mode,Priority,SignalID,Polarity,RequestNumber,SyncSignalID,SyncPolarity,SyncEnable,EventEnable,SyncRequestNumber
Dma.ADC3.2.SignalID=NONE
Dma.ADC3.2.SyncEnable=DISABLE
Dma.ADC3.2.SyncPolarity=HAL_DMAMUX_SYNC_NO_EVENT
Dma.ADC3.2.SyncRequestNumber=1
Dma.ADC3.2.SyncSignalID=NONE
Dma.ADC4.3.Direction=DMA_PERIPH_TO_MEMORY
Dma.ADC4.3.EventEnable=DISABLE
Dma.ADC4.3.Instance=DMA1_Channel4
Dma.ADC4.3.MemDataAlignment=DMA_MDATAALIGN_HALFWORD
Dma.ADC4.3.MemInc=DMA_MINC_ENABLE
Dma.ADC4.3.Mode=DMA_NORMAL
Dma.ADC4.3.PeriphDataAlignment=DMA_PDATAALIGN_HALFWORD
Dma.ADC4.3.PeriphInc=DMA_PINC_DISABLE
Dma.ADC4.3.Polarity=HAL_DMAMUX_REQ_GEN_RISING
Dma.ADC4.3.Priority=DMA_PRIORITY_LOW
Dma.ADC4.3.RequestNumber=1
Dma.ADC4.3.RequestParameters=Instance,Direction,PeriphInc,MemInc,PeriphDataAlignment,MemDataAlignment,Mode,Priority,SignalID,Polarity,RequestNumber,SyncSignalID,SyncPolarity,SyncEnable,EventEnable,SyncRequestNumber
Dma.ADC4.3.SignalID=NONE
Dma.ADC4.3.SyncEnable=DISABLE
Dma.ADC4.3.SyncPolarity=HAL_DMAMUX_SYNC_NO_EVENT
Dma.ADC4.3.SyncRequestNumber=1
Dma.ADC4.3.SyncSignalID=NONE
Dma.Request0=ADC1
Dma.Request1=ADC2
Dma.Request2=ADC3
Dma.Request3=ADC4
Dma.RequestsNb=4
FREERTOS.IPParameters=Tasks01,configENABLE_FPU
FREERTOS.Tasks01=defaultTask,24,128,StartDefaultTask,Default,NULL,Dynamic,NULL,NULL
FREERTOS.configENABLE_FPU=1
File.Version=6
GPIO.groupedBy=Group By Peripherals
I2C2.IPParameters=Timing
I2C2.Timing=0x60505F8C
KeepUserPlacement=false
Mcu.CPN=STM32G474VBT6
Mcu.Family=STM32G4
Mcu.IP0=ADC1
Mcu.IP1=ADC2
Mcu.IP10=RCC
Mcu.IP11=SPI1
Mcu.IP12=SYS
Mcu.IP13=TIM1
Mcu.IP14=TIM2
Mcu.IP15=TIM3
Mcu.IP16=TIM4
Mcu.IP17=TIM5
Mcu.IP18=TIM8
Mcu.IP19=USART3
Mcu.IP2=ADC3
Mcu.IP20=USB
Mcu.IP21=USB_DEVICE
Mcu.IP3=ADC4
Mcu.IP4=CORDIC
Mcu.IP5=DMA
Mcu.IP6=FREERTOS
Mcu.IP7=I2C2
Mcu.IP8=IWDG
Mcu.IP9=NVIC
Mcu.IPNb=22
Mcu.Name=STM32G474V(B-C-E)Tx
Mcu.Package=LQFP100
Mcu.Pin0=PE2
Mcu.Pin1=PE3
Mcu.Pin10=PA1
Mcu.Pin11=PA3
Mcu.Pin12=PA4
Mcu.Pin13=PA5
Mcu.Pin14=PA6
Mcu.Pin15=PA7
Mcu.Pin16=PC4
Mcu.Pin17=PB1
Mcu.Pin18=PB2
Mcu.Pin19=PE7
Mcu.Pin2=PE4
Mcu.Pin20=PE8
Mcu.Pin21=PE9
Mcu.Pin22=PE10
Mcu.Pin23=PE11
Mcu.Pin24=PE12
Mcu.Pin25=PE14
Mcu.Pin26=PE15
Mcu.Pin27=PB10
Mcu.Pin28=PB11
Mcu.Pin29=PB12
Mcu.Pin3=PC13
Mcu.Pin30=PB13
Mcu.Pin31=PB14
Mcu.Pin32=PD9
Mcu.Pin33=PD10
Mcu.Pin34=PD11
Mcu.Pin35=PD12
Mcu.Pin36=PD13
Mcu.Pin37=PD14
Mcu.Pin38=PC6
Mcu.Pin39=PC7
Mcu.Pin4=PF0-OSC_IN
Mcu.Pin40=PC8
Mcu.Pin41=PA8
Mcu.Pin42=PA9
Mcu.Pin43=PA10
Mcu.Pin44=PA11
Mcu.Pin45=PA12
Mcu.Pin46=PA13
Mcu.Pin47=PA14
Mcu.Pin48=PA15
Mcu.Pin49=PC12
Mcu.Pin5=PG10-NRST
Mcu.Pin50=PD2
Mcu.Pin51=PD3
Mcu.Pin52=PD4
Mcu.Pin53=PD7
Mcu.Pin54=PB3
Mcu.Pin55=PB4
Mcu.Pin56=PB5
Mcu.Pin57=PB6
Mcu.Pin58=PB7
Mcu.Pin59=PB8-BOOT0
Mcu.Pin6=PC1
Mcu.Pin60=PE0
Mcu.Pin61=VP_CORDIC_VS_CORDIC
Mcu.Pin62=VP_FREERTOS_VS_CMSIS_V2
Mcu.Pin63=VP_IWDG_VS_IWDG
Mcu.Pin64=VP_SYS_VS_tim6
Mcu.Pin65=VP_SYS_VS_DBSignals
Mcu.Pin66=VP_USB_DEVICE_VS_USB_DEVICE_CDC_FS
Mcu.Pin7=PC2
Mcu.Pin8=PC3
Mcu.Pin9=PA0
Mcu.PinsNb=67
Mcu.ThirdPartyNb=0
Mcu.UserConstants=
Mcu.UserName=STM32G474VBTx
MxCube.Version=6.6.1
MxDb.Version=DB.6.0.60
NVIC.BusFault_IRQn=true\:0\:0\:false\:false\:true\:false\:false\:false\:false
NVIC.DMA1_Channel1_IRQn=true\:5\:0\:false\:false\:true\:true\:false\:true\:true
NVIC.DMA1_Channel2_IRQn=true\:5\:0\:false\:false\:true\:true\:false\:true\:true
NVIC.DMA1_Channel3_IRQn=true\:5\:0\:false\:false\:true\:true\:false\:true\:true
NVIC.DMA1_Channel4_IRQn=true\:5\:0\:false\:false\:true\:true\:false\:true\:true
NVIC.DebugMonitor_IRQn=true\:0\:0\:false\:false\:true\:false\:false\:false\:false
NVIC.ForceEnableDMAVector=true
NVIC.HardFault_IRQn=true\:0\:0\:false\:false\:true\:false\:false\:false\:false
NVIC.MemoryManagement_IRQn=true\:0\:0\:false\:false\:true\:false\:false\:false\:false
NVIC.NonMaskableInt_IRQn=true\:0\:0\:false\:false\:true\:false\:false\:false\:false
NVIC.PendSV_IRQn=true\:15\:0\:false\:false\:false\:true\:false\:false\:false
NVIC.PriorityGroup=NVIC_PRIORITYGROUP_4
NVIC.SVCall_IRQn=true\:0\:0\:false\:false\:false\:false\:false\:false\:false
NVIC.SavedPendsvIrqHandlerGenerated=true
NVIC.SavedSvcallIrqHandlerGenerated=true
NVIC.SavedSystickIrqHandlerGenerated=true
NVIC.SysTick_IRQn=true\:15\:0\:false\:false\:false\:true\:false\:true\:false
NVIC.TIM6_DAC_IRQn=true\:15\:0\:false\:false\:true\:false\:false\:true\:true
NVIC.TimeBase=TIM6_DAC_IRQn
NVIC.TimeBaseIP=TIM6
NVIC.USB_LP_IRQn=true\:5\:0\:false\:false\:true\:true\:false\:true\:true
NVIC.UsageFault_IRQn=true\:0\:0\:false\:false\:true\:false\:false\:false\:false
PA0.Locked=true
PA0.Mode=IN1-Single-Ended
PA0.Signal=ADC1_IN1
PA1.Mode=IN2-Single-Ended
PA1.Signal=ADC1_IN2
PA10.Locked=true
PA10.Signal=S_TIM1_CH3
PA11.Locked=true
PA11.Mode=Device
PA11.Signal=USB_DM
PA12.Locked=true
PA12.Mode=Device
PA12.Signal=USB_DP
PA13.Locked=true
PA13.Mode=Serial_Wire
PA13.Signal=SYS_JTMS-SWDIO
PA14.Locked=true
PA14.Mode=Serial_Wire
PA14.Signal=SYS_JTCK-SWCLK
PA15.Signal=S_TIM2_CH1
PA3.Locked=true
PA3.Signal=GPIO_Output
PA4.Locked=true
PA4.Signal=GPIO_Output
PA5.Mode=Full_Duplex_Master
PA5.Signal=SPI1_SCK
PA6.Locked=true
PA6.Mode=IN3-Single-Ended
PA6.Signal=ADC2_IN3
PA7.Locked=true
PA7.Mode=IN4-Single-Ended
PA7.Signal=ADC2_IN4
PA8.Locked=true
PA8.Signal=S_TIM1_CH1
PA9.Locked=true
PA9.Signal=S_TIM1_CH2
PB1.Mode=IN1-Single-Ended
PB1.Signal=ADC3_IN1
PB10.Mode=Asynchronous
PB10.Signal=USART3_TX
PB11.Mode=Asynchronous
PB11.Signal=USART3_RX
PB12.Locked=true
PB12.Signal=GPIO_Output
PB13.Locked=true
PB13.Signal=GPIO_Output
PB14.Locked=true
PB14.Signal=GPIO_Output
PB2.Signal=S_TIM5_CH1
PB3.Locked=true
PB3.Signal=SYS_JTDO-SWO
PB4.Locked=true
PB4.Mode=Full_Duplex_Master
PB4.Signal=SPI1_MISO
PB5.Locked=true
PB5.Mode=Full_Duplex_Master
PB5.Signal=SPI1_MOSI
PB6.Locked=true
PB6.Signal=GPIO_Output
PB7.Locked=true
PB7.Signal=GPIO_Output
PB8-BOOT0.Locked=true
PC1.Locked=true
PC1.Signal=GPIO_Output
PC12.Signal=S_TIM5_CH2
PC13.Locked=true
PC13.Signal=GPIO_Output
PC2.Locked=true
PC2.Signal=GPIO_Output
PC3.Locked=true
PC3.Signal=GPIO_Input
PC4.Mode=I2C
PC4.Signal=I2C2_SCL
PC6.Locked=true
PC6.Signal=S_TIM8_CH1
PC7.Locked=true
PC7.Signal=S_TIM8_CH2
PC8.Locked=true
PC8.Signal=S_TIM8_CH3
PCC.Checker=true
PCC.Line=STM32G4x4
PCC.MCU=STM32G474V(B-C-E)Tx
PCC.PartNumber=STM32G474VBTx
PCC.Seq0=2
PCC.Seq0.Step0.Average_Current=42.82 mA
PCC.Seq0.Step0.CPU_Frequency=170 MHz
PCC.Seq0.Step0.Category=In DS Table
PCC.Seq0.Step0.DMIPS=212.5
PCC.Seq0.Step0.Duration=0.1 ms
PCC.Seq0.Step0.Frequency=4 MHz
PCC.Seq0.Step0.Memory=FLASH/DualBank/ART
PCC.Seq0.Step0.Mode=RUN
PCC.Seq0.Step0.Oscillator=HSE BYP PLL
PCC.Seq0.Step0.Peripherals=ADC1 ADC2 ADC3 ADC4 CORDIC GPIOA GPIOB GPIOC GPIOD GPIOE I2C1 SPI1 TIM1 TIM2 TIM3 TIM4 TIM5 TIM8 USART2 USB
PCC.Seq0.Step0.TaMax=120.24
PCC.Seq0.Step0.User's_Consumption=0 mA
PCC.Seq0.Step0.Vcore=Range1-Boost
PCC.Seq0.Step0.Vdd=3.0
PCC.Seq0.Step0.Voltage_Source=Battery
PCC.Seq0.Step1.Average_Current=80.5 \u00B5A
PCC.Seq0.Step1.CPU_Frequency=0 Hz
PCC.Seq0.Step1.Category=In DS Table
PCC.Seq0.Step1.DMIPS=0.0
PCC.Seq0.Step1.Duration=0.9 ms
PCC.Seq0.Step1.Frequency=0 Hz
PCC.Seq0.Step1.Memory=NA
PCC.Seq0.Step1.Mode=STOP1
PCC.Seq0.Step1.Oscillator=ALL CLOCKS OFF
PCC.Seq0.Step1.Peripherals=
PCC.Seq0.Step1.TaMax=129.98
PCC.Seq0.Step1.User's_Consumption=0 mA
PCC.Seq0.Step1.Vcore=NoRange
PCC.Seq0.Step1.Vdd=3.0
PCC.Seq0.Step1.Voltage_Source=Battery
PCC.Series=STM32G4
PCC.Temperature=25
PCC.Vdd=3.0
PD10.Locked=true
PD10.Signal=GPIO_Output
PD11.Locked=true
PD11.Signal=GPIO_Input
PD12.Locked=true
PD12.Signal=S_TIM4_CH1
PD13.Locked=true
PD13.Signal=S_TIM4_CH2
PD14.Locked=true
PD14.Signal=S_TIM4_CH3
PD2.Signal=S_TIM3_ETR
PD3.Signal=S_TIM2_ETR
PD4.Signal=S_TIM2_CH2
PD7.Locked=true
PD7.Signal=S_TIM2_CH3
PD9.Locked=true
PD9.Signal=GPIO_Output
PE0.Locked=true
PE0.Signal=GPIO_Output
PE10.Locked=true
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

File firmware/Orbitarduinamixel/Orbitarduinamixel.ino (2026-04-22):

// Select board "Generic STM32G4 series"
// and board part number "Generic G474VBTx"

#include <SimpleFOC.h>
#include <SimpleFOCDrivers.h>
#include "encoders/as5047/MagneticSensorAS5047.h"
#include <BMI088.h>
// #include <Filters.h>
// #include <Filters/Butterworth.hpp>
#include <CMSIS_DSP.h>
#include <Dynamixel2Arduino.h>
#include <IWatchdog.h>

// Firmware Revision (odd = dev, even = stable)
#define ORBITARDUINAMIXEL_REV  1 // Dev for first release

uint8_t orbita_firmware_rev = ORBITARDUINAMIXEL_REV;


#define GREEN_LED  PE_0
#define RED_LED    PC13
#define TEST_PIN_2 PB12 // Now used as Bot_Motor_Phase_B
#define TEST_PIN_3 PB13 // Now used as Bot_Motor_Phase_C
#define TEST_PIN_4 PA7

#define WATCHDOG_DELAY 4000000 // us

//      Top

const byte topCSA     = PA0;
const byte topCSB     = PA1;
const byte topEncA    = PA8;
const byte topEncB    = PA9;
const byte topEncI    = PE_7;
const byte topHallA   = PA8;
const byte topHallB   = PA9;
const byte topHallC   = PA10;
const byte topMotA    = PD_12;
const byte topMotB    = PD_13;
const byte topMotC    = PD_14;
const byte topMotEn   = PD_9;
const byte topMotnRST = PD_10;
const byte topMotnFlt = PD_11;
#define TOP_MOTOR_CMD 'T'

//      Middle
const byte midCSA     = PB1;
const byte midCSB     = PE_9;
const byte midEncA    = PA15;
const byte midEncB    = PD_4;
const byte midEncI    = PD_3;
const byte midHallA   = PA15;
const byte midHallB   = PD_4;
const byte midHallC   = PD_7;
const byte midMotA    = PB2;
const byte midMotB    = PC_12;
const byte midMotC    = PE_8;
const byte midMotEn   = PC_1;
const byte midMotnRST = PC_2;
const byte midMotnFlt = PC_3;
#define MID_MOTOR_CMD 'M'

//      Bottom
const byte botCSA     = PE_14;
const byte botCSB     = PE_15;
const byte botEncA    = PE_2;
const byte botEncB    = PE_3;
const byte botEncI    = PD_2;
const byte botHallA   = PE_2;
const byte botHallB   = PE_6; // PE3 on Houston-A1 base
const byte botHallC   = PC_0; // PE4 on Houston-A1 base
const byte botMotA    = PC6;
const byte botMotB    = PC_7;
const byte botMotC    = PC_8;
const byte botMotEn   = PE_10;
const byte botMotnRST = PE_11;
const byte botMotnFlt = PE_12;
#define BOT_MOTOR_CMD 'B'


//      Orbita Magnetic Sensor
const byte orbitaSPI_MOSI  = PB5;
const byte orbitaSPI_MISO  = PB4;
const byte orbitaSPI_SCK   = PA5;
const byte orbitaTopSPI_CS = PA4;
const byte orbitaMidSPI_CS = PB7;
const byte orbitaBotSPI_CS = PB6;
#define ORBITA_SENSOR_TYPE AS5047_SPI

//      Orbita IMU
const byte orbitaIMU_Acc_CS = PA3;
const byte orbitaIMU_Gyr_CS = PB9;

/************************ Motors ***********************/
// Maxon ECX Torque 22 M
#define MOTOR_POLE_PAIRS                4
#define MOTOR_PHASE_RESISTANCE          0.763
#define MOTOR_SPEED_COEFF             645.0
// Maxon ENX 22 (encoder)
#define MOTOR_ENCODER_NB_STEPS        512
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

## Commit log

2026-04-09 figure generation for poster
    [Test1.csv]
2026-04-09 camera demo should be working with venv
2026-04-09 don't need poster stuff
    [Test1.csv]
2026-04-22 Add orbita3d_control
    [test_input.csv]
2026-04-22 Remove uneeded files
    [test_input.csv]
2026-04-23 docker process should work if you can pass the device
2026-05-01 Add custom hardware (electronics and parts)
    [ASE00037-C1_carte_Houston_BOM.xlsx, ASE00037-C1_carte_Houston_POS.csv, BottomPinion.STEP, BottomPinion_Dslot.STEP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]
